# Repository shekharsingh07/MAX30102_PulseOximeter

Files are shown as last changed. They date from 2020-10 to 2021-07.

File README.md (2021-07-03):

## **Project Name:** MAX30102 Fingertip Pulse Oximeter

**Table of Contents:**
<ol>
  <li>Description</li>
  <li>License</li>
</ol>

**Description:** <br>For my undergraduate thesis, I designed a PCB for a fingertip Pulse oximeter. The pulse oximeter would use Maxim Integrated's MAX30102 biometric sensor and is created for 24hr monitoring.
<br>The project is divided into two sections:
<ol>
  <li>The embbeded software design:
    <ul>
      <li>Which is further subdivided into sections based on the components - the memory, the I/O system, and the sensor</li>
      <li>The embedded design revolves around the STM32G071RB microcontroller</li>
    </ul>
  </li>
  <li>The PCB design:
    <ul>
      <li>Which contains the necessary files to manufacture this Pulse Oximeter PCB.</li>
    </ul>
  </li>
</ol>

**License:** MIT license

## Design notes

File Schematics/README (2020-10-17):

The schematics and PCB designs have been done using KiCAD.

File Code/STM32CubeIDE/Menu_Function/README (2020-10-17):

This is the basic menu functinoality of the device. All code was done in STM32CubeIDE for a NUCLEO-G071RB. The end microcontroller that would be used is the STM32G071G8U6.

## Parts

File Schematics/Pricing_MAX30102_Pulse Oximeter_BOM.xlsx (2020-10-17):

Id | Designator | Package | Quantity | Designation | Supplier | Reference | Part No. | Total Components | Unit Price ($) | Price ($)
2 | C1,C4,C5 | C_0603_1608Metric | 3 | 4.7uF | Digi-Key | https://www.digikey.com/products/en?keywords=1276-1045-1-ND | 1276-1045-1-ND | 15 | 0.041 | 0.615
3 | C2,C3 | C_0603_1608Metric | 2 | 1uF | Digi-Key | https://www.digikey.com/products/en?keywords=1276-1945-1-ND | 1276-1945-1-ND | 10 | 0.029 | 0.29
4 | C6 | C_0603_1608Metric | 1 | 10uF | Digi-Key | https://www.digikey.com/products/en?keywords=1276-1119-1-ND | 1276-1119-1-ND | 5 | 0.11 | 0.55
5 | C7,C8 | C_0603_1608Metric | 2 | 0.1uF | Digi-Key | https://www.digikey.com/products/en?keywords=1276-1935-1-ND | 1276-1935-1-ND | 10 | 0.021 | 0.21
6 | D1 | LED_0603_1608Metric | 1 | RED | Digi-Key | https://www.digikey.com/products/en?keywords=732-4978-1-ND | 732-4978-1-ND | 5 | 0.14 | 0.7
7 | D4,D5,D6 | LED_0603_1608Metric | 3 | RED | Digi-Key | https://www.digikey.com/products/en?keywords=732-4978-1-ND | 732-4978-1-ND | 15 | 0.14 | 2.1
8 | F1 | C2Q250 | 1 | 250mA | Digi-Key | https://www.digikey.com/products/en?keywords=507-1086-1-ND | 507-1086-1-ND | 5 | 0.28 | 1.39
11 | IC1 | STM32G0_UFQFPN28_T1 | 1 | STM32G071G8U6 | Digi-Key | https://www.digikey.com/products/en?keywords=497-STM32G071G8U6-ND | 497-STM32G071G8U6-ND | 5 | 3.02 | 15.1
12 | J1 | USB_Micro-B_Molex_47346-0001 | 1 | USB_B_Micro | Digi-Key | https://www.digikey.com/products/en?keywords=609-4613-2-ND | 609-4613-2-ND | 1 | 0.2149 | 0.2149
19 | R1,R2,R4,R15,R16,R17,R18,R19,R21 | R_0603_1608Metric | 9 | 1.8K [ohm] | Digi-Key | https://www.digikey.com/products/en?keywords=RMCF0603JT1K80CT-ND | RMCF0603JT1K80CT-ND | 45 | 0.013 | 0.585
20 | R3,R5,R6 | R_0603_1608Metric | 3 | 10K [ohm] | Digi-Key | https://www.digikey.com/products/en?keywords=RMCF0603JT10K0CT-ND | RMCF0603JT10K0CT-ND | 15 | 0.013 | 0.195
21 | R7,R8,R9,R10,R11,R12,R13,R14,R23,R24,R25,R26 | R_0603_1608Metric | 12 | 0 ohm | Digi-Key | https://www.digikey.com/products/en?keywords=RMCF0603ZT0R00CT-ND | RMCF0603ZT0R00CT-ND | 60 | 0.1 | 6
22 | SW1,SW2 | SW_SPST_B3U-1000P | 2 | SW_Push | Digi-Key | https://www.digikey.com/products/en?keywords=SW1020CT-ND | SW1020CT-ND | 10 | 0.92 | 9.2
23 | U1 | MCP73811T-420I&slash_OT | 1 | MCP73811T-420I_OT | Digi-Key | https://www.digikey.com/products/en?keywords=MCP73811T-420I%2FOTCT-ND | MCP73811T-420I/OTCT-ND | 5 | 0.51 | 2.55
24 | U2 | MIC94310-GYM5-SOT-753 | 1 | MIC94310 | Digi-Key | https://www.digikey.com/products/en?keywords=576-4769-1-ND | 576-4769-1-ND | 5 | 0.23 | 1.15
25 | U3 | MAX30102EFD&plus_ | 1 | MAX30102EFD+ | Digi-Key | https://www.digikey.com/products/en?keywords=MAX30102EFD%2B-ND | MAX30102EFD+-ND | 5 | 7.74 | 38.7
26 | U4 | SON127P500X600X60-9N | 1 | AT45DB081E-MHN-Y | Digi-Key | https://www.digikey.com/products/en?keywords=1265-1110-ND | 1265-1110-ND | 5 | 1.64 | 8.2
27 | U5,U6 | MMBT3906-7-F | 2 | MMBT3906-7-F | Digi-Key | https://www.digikey.com/products/en?keywords=MMBT3906-FDICT-ND | MMBT3906-FDICT-ND | 10 | 0.12 | 1.2
 |  |  |  |  |  |  | Total | 231 | 15.2819 | 88.9499

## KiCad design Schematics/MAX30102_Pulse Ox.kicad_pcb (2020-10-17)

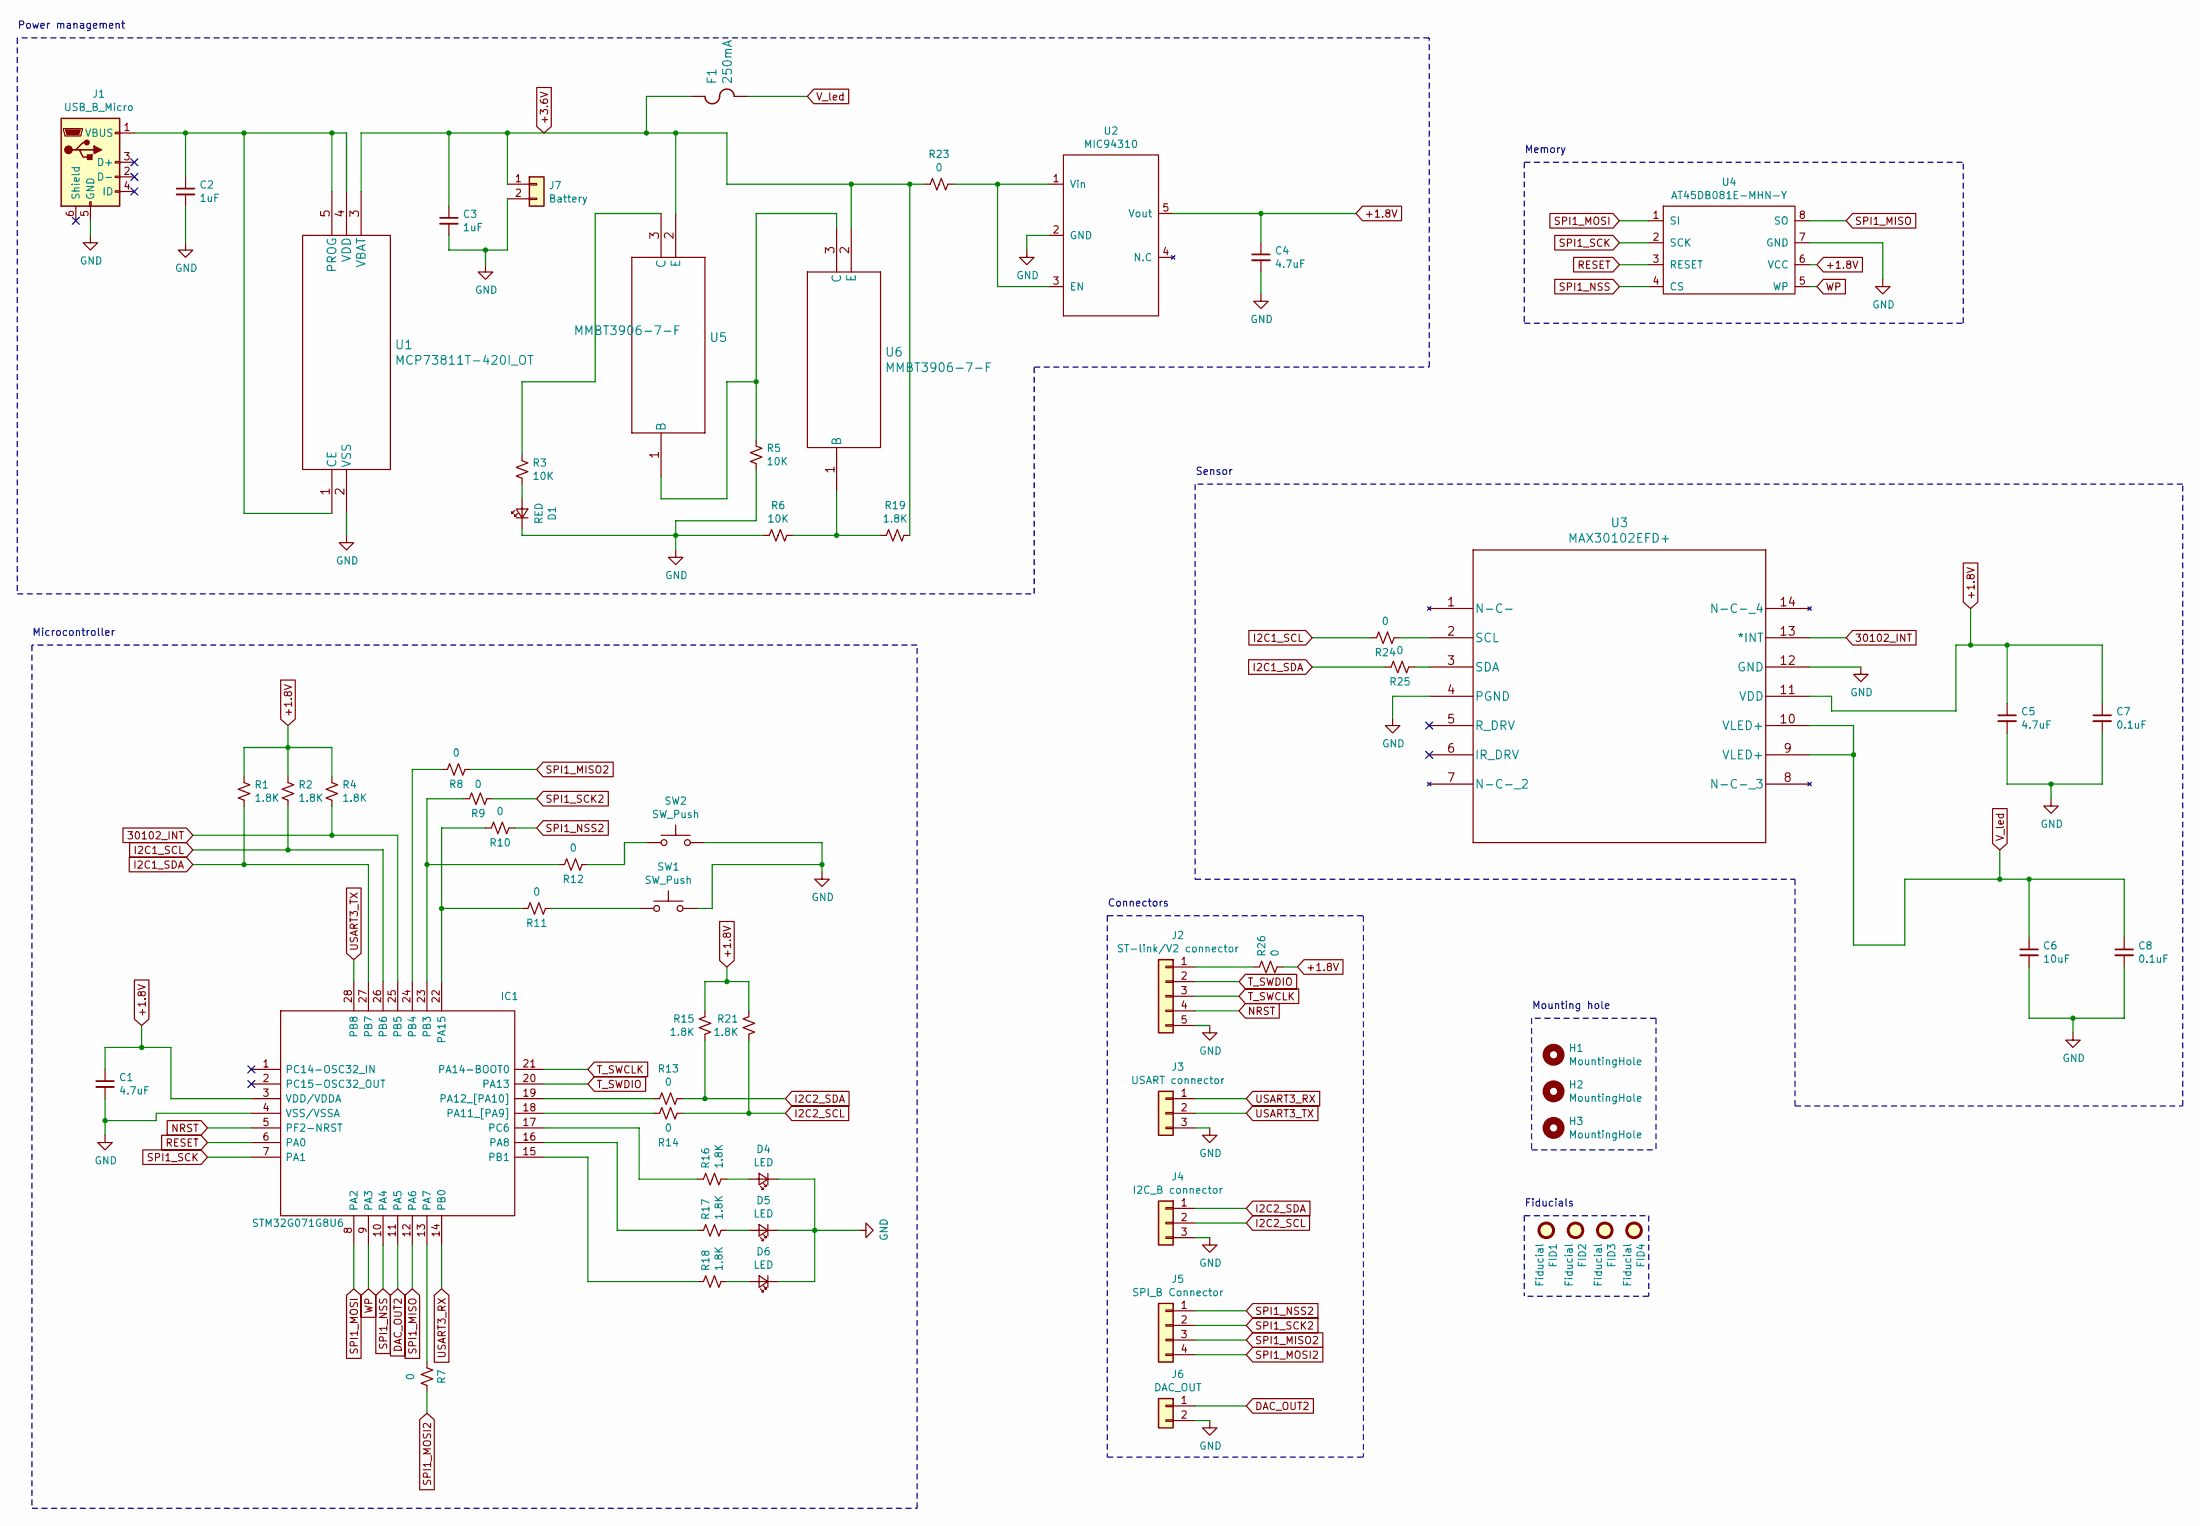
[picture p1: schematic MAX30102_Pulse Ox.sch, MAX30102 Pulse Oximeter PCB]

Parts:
C1, C4, C5: 4.7uF; C_0603_1608Metric
C2, C3: 1uF; C_0603_1608Metric
C6: 10uF; C_0603_1608Metric
C7, C8: 0.1uF; C_0603_1608Metric
D1: RED; LED_0603_1608Metric
D4, D5, D6: LED; LED_0603_1608Metric
F1: 250mA; C2Q250
FID1, FID2, FID3, FID4: Fiducial; Fiducial_1mm_Mask2mm
H1, H2, H3: MountingHole; MountingHole_2.1mm
IC1: STM32G071G8U6; STM32G0_UFQFPN28_T1; Manufacturer_Part_Number STM32G071G8U6; Mouser Part Number 511-STM32G071G8U6
J1: USB_B_Micro; USB_Micro-B_Molex_47346-0001
J2: ST-link/V2 connector; SolderWirePad_1x05_SMD
J3: USART connector; SolderWirePad_1x03_SMD
J4: I2C_B connector; SolderWirePad_1x03_SMD
J5: SPI_B Connector; SolderWirePad_1x04_SMD
J6: DAC_OUT; SolderWirePad_1x02_SMD
J7: Battery; SolderWirePad_1x02_SMD
R1, R2, R4, R15, R16, R17, R18, R19, R21: 1.8K; R_0603_1608Metric
R3, R5, R6: 10K; R_0603_1608Metric
R7, R8, R9, R10, R11, R12, R13, R14, R23, R24, R25, R26: 0; R_0603_1608Metric
SW1, SW2: SW_Push; SW_SPST_B3U-1000P
U1: MCP73811T-420I_OT; MCP73811T-420I&slash_OT
U2: MIC94310; MIC94310-GYM5-SOT-753
U3: MAX30102EFD+; MAX30102EFD&plus_
U4: AT45DB081E-MHN-Y; SON127P500X600X60-9N
U5, U6: MMBT3906-7-F

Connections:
30102_INT: IC1.25 (PB5), R4.2, U3.13 (*INT)
+1.8V: C1.1, C4.1, C5.1, C7.1, IC1.3 (VDD/VDDA), R1.1, R2.1, R4.1, R15.1, R21.1, R26.2, U2.5 (Vout), U3.11 (VDD), U4.6 (VCC)
+3.6V: C3.1, F1.2, J7.1, R19.1, R23.2, U1.3 (VBAT), U5.2 (E), U6.2 (E)
DAC_OUT2: IC1.11 (PA5), J6.1
GND: C1.2, C2.2, C3.2, C4.2, C5.2, C6.2, C7.2, C8.2, D1.1 (K), D4.1 (K), D5.1 (K), D6.1 (K), IC1.4 (VSS/VSSA), J1.5 (GND), J2.5, J3.3, J4.3, J6.2, J7.2, R5.2, R6.2, SW1.2, SW2.2, U1.2 (VSS), U2.2 (GND), U3.4 (PGND), U3.12 (GND), U4.7 (GND)
I2C1_SCL: IC1.26 (PB6), R2.2, R24.1
I2C1_SDA: IC1.27 (PB7), R1.2, R25.1
I2C2_SCL: J4.2, R14.2, R21.2
I2C2_SDA: J4.1, R13.2, R15.2
NRST: IC1.5 (PF2-NRST), J2.4
unnamed: C2.1, J1.1 (VBUS), U1.1 (CE), U1.4 (VDD), U1.5 (PROG)
unnamed: D1.2 (A), R3.2
unnamed: D4.2 (A), R16.1
unnamed: D5.2 (A), R17.1
unnamed: D6.2 (A), R18.1
unnamed: IC1.13 (PA7), R7.2
unnamed: IC1.15 (PB1), R18.2
unnamed: IC1.16 (PA8), R17.2
unnamed: IC1.17 (PC6), R16.2
unnamed: IC1.18 (PA11_[PA9]), R14.1
unnamed: IC1.19 (PA12_[PA10]), R13.1
unnamed: IC1.22 (PA15), R10.1, R11.1
unnamed: IC1.23 (PB3), R9.1, R12.1
unnamed: IC1.24 (PB4), R8.1
unnamed: J2.1, R26.1
unnamed: R3.1, U5.3 (C)
unnamed: R5.1, U5.1 (B), U6.3 (C)
unnamed: R11.2, SW1.1
unnamed: R12.2, SW2.1
unnamed: R6.1, R19.2, U6.1 (B)
unnamed: R23.1, U2.1 (Vin), U2.3 (EN)
unnamed: R24.2, U3.2 (SCL)
unnamed: R25.2, U3.3 (SDA)
RESET: IC1.6 (PA0), U4.3 (RESET)
SPI1_MISO: IC1.12 (PA6), U4.8 (SO)
SPI1_MISO2: J5.3, R8.2
SPI1_MOSI: IC1.8 (PA2), U4.1 (SI)
SPI1_MOSI2: J5.4, R7.1
SPI1_NSS: IC1.10 (PA4), U4.4 (CS)
SPI1_NSS2: J5.1, R10.2
SPI1_SCK: IC1.7 (PA1), U4.2 (SCK)
SPI1_SCK2: J5.2, R9.2
T_SWCLK: IC1.21 (PA14-BOOT0), J2.3
T_SWDIO: IC1.20 (PA13), J2.2
USART3_RX: IC1.14 (PB0), J3.1
USART3_TX: IC1.28 (PB8), J3.2
V_led: C6.1, C8.1, F1.1, U3.9 (VLED+), U3.10 (VLED+)
WP: IC1.9 (PA3), U4.5 (WP)

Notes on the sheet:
Microcontroller
Power management
Connectors
Sensor
Memory
Mounting hole
Fiducials

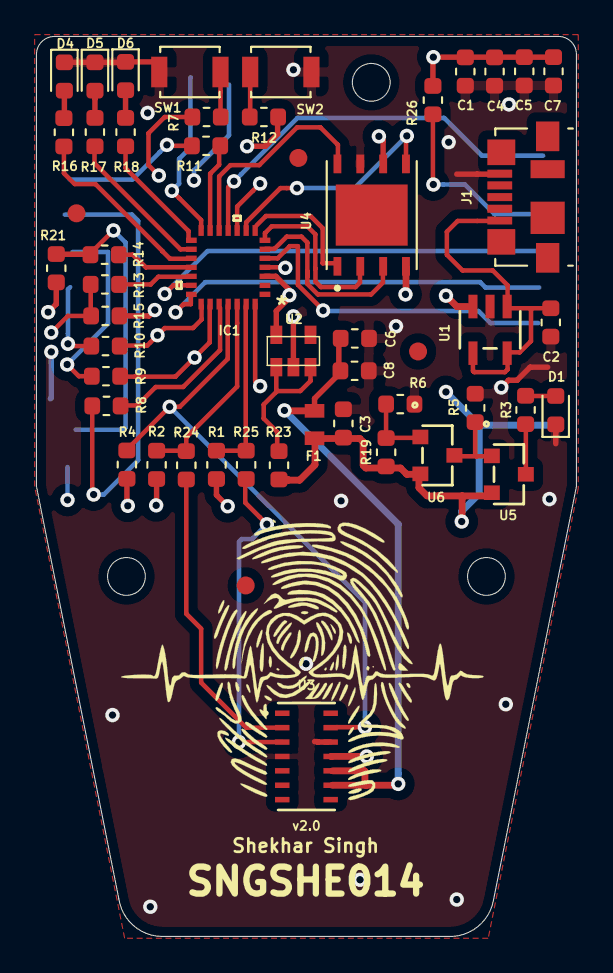
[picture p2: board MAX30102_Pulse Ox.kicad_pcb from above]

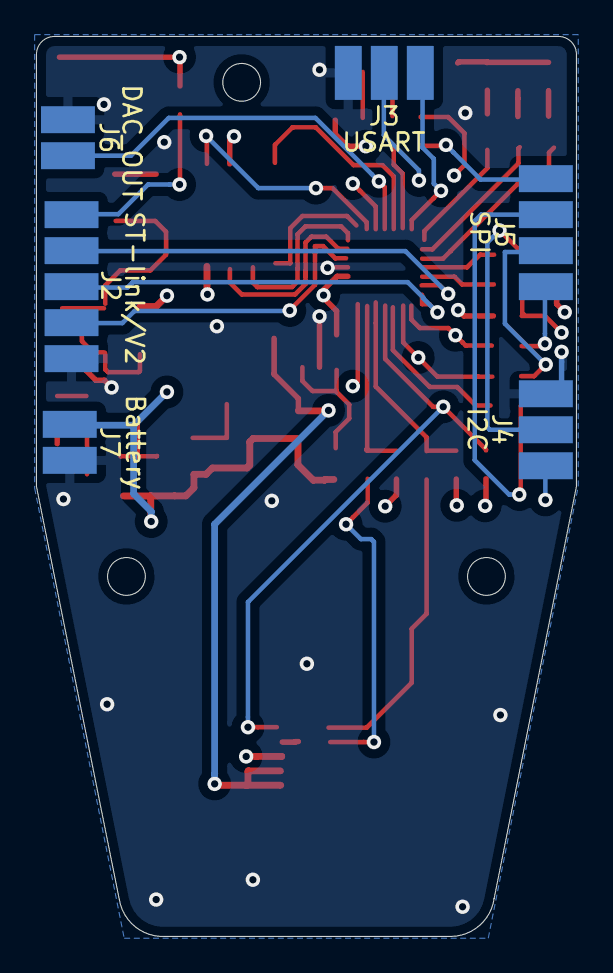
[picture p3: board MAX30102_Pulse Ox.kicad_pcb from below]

Board: 4 copper layers, 30.0 x 50.0 mm, 60 parts (6 on the bottom side), 48 nets.

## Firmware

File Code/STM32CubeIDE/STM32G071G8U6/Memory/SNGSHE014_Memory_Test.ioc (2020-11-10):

#MicroXplorer Configuration settings - do not modify
File.Version=6
GPIO.groupedBy=Group By Peripherals
KeepUserPlacement=false
Mcu.Family=STM32G0
Mcu.IP0=NVIC
Mcu.IP1=RCC
Mcu.IP2=SPI1
Mcu.IP3=SYS
Mcu.IP4=USART3
Mcu.IPNb=5
Mcu.Name=STM32G071G(6-8-B)Ux
Mcu.Package=UFQFPN28
Mcu.Pin0=PA0
Mcu.Pin1=PA1
Mcu.Pin2=PA2
Mcu.Pin3=PA3
Mcu.Pin4=PA4
Mcu.Pin5=PA6
Mcu.Pin6=PB0
Mcu.Pin7=PB8
Mcu.Pin8=VP_SYS_VS_Systick
Mcu.Pin9=VP_SYS_VS_DBSignals
Mcu.PinsNb=10
Mcu.ThirdPartyNb=0
Mcu.UserConstants=
Mcu.UserName=STM32G071G8Ux
MxCube.Version=6.0.1
MxDb.Version=DB.6.0.0
NVIC.ForceEnableDMAVector=true
NVIC.HardFault_IRQn=true\:0\:0\:false\:false\:true\:false\:false
NVIC.NonMaskableInt_IRQn=true\:0\:0\:false\:false\:true\:false\:false
NVIC.PendSV_IRQn=true\:0\:0\:false\:false\:true\:false\:false
NVIC.SPI1_IRQn=true\:0\:0\:false\:false\:true\:true\:true
NVIC.SVC_IRQn=true\:0\:0\:false\:false\:true\:false\:false
NVIC.SysTick_IRQn=true\:0\:0\:false\:false\:true\:false\:true
NVIC.USART3_4_LPUART1_IRQn=true\:0\:0\:false\:false\:true\:true\:true
PA0.GPIOParameters=GPIO_Label
PA0.GPIO_Label=RESET
PA0.Locked=true
PA0.Signal=GPIO_Output
PA1.Mode=Full_Duplex_Master
PA1.Signal=SPI1_SCK
PA2.Mode=Full_Duplex_Master
PA2.Signal=SPI1_MOSI
PA3.GPIOParameters=GPIO_Label
PA3.GPIO_Label=WP
PA3.Locked=true
PA3.Signal=GPIO_Output
PA4.Mode=NSS_Signal_Hard_Output
PA4.Signal=SPI1_NSS
PA6.Mode=Full_Duplex_Master
PA6.Signal=SPI1_MISO
PB0.Mode=Asynchronous
PB0.Signal=USART3_RX
PB8.Locked=true
PB8.Mode=Asynchronous
PB8.Signal=USART3_TX
PinOutPanel.RotationAngle=0
ProjectManager.AskForMigrate=true
ProjectManager.BackupPrevious=false
ProjectManager.CompilerOptimize=6
ProjectManager.ComputerToolchain=false
ProjectManager.CoupleFile=false
ProjectManager.CustomerFirmwarePackage=
ProjectManager.DefaultFWLocation=true
ProjectManager.DeletePrevious=true
ProjectManager.DeviceId=STM32G071G8Ux
ProjectManager.FirmwarePackage=STM32Cube FW_G0 V1.3.0
ProjectManager.FreePins=false
ProjectManager.HalAssertFull=false
ProjectManager.HeapSize=0x200
ProjectManager.KeepUserCode=true
ProjectManager.LastFirmware=true
ProjectManager.LibraryCopy=1
ProjectManager.MainLocation=Core/Src
ProjectManager.NoMain=false
ProjectManager.PreviousToolchain=STM32CubeIDE
ProjectManager.ProjectBuild=false
ProjectManager.ProjectFileName=SNGSHE014_Memory_Test.ioc
ProjectManager.ProjectName=SNGSHE014_Memory_Test
ProjectManager.RegisterCallBack=
ProjectManager.StackSize=0x400
ProjectManager.TargetToolchain=STM32CubeIDE
ProjectManager.ToolChainLocation=
ProjectManager.UnderRoot=true
ProjectManager.functionlistsort=1-MX_GPIO_Init-GPIO-false-HAL-true,2-SystemClock_Config-RCC-false-HAL-false,3-MX_SPI1_Init-SPI1-false-HAL-true,4-MX_USART3_UART_Init-USART3-false-HAL-true
RCC.AHBFreq_Value=16000000
RCC.APBFreq_Value=16000000
RCC.APBTimFreq_Value=16000000
RCC.CECFreq_Value=32786.88524590164
RCC.CortexFreq_Value=16000000
RCC.EXTERNAL_CLOCK_VALUE=48000
RCC.FCLKCortexFreq_Value=16000000
RCC.FamilyName=M
RCC.HCLKFreq_Value=16000000
RCC.HSE_VALUE=8000000
RCC.HSI_VALUE=16000000
RCC.I2C1Freq_Value=16000000
RCC.I2S1Freq_Value=16000000
RCC.IPParameters=AHBFreq_Value,APBFreq_Value,APBTimFreq_Value,CECFreq_Value,CortexFreq_Value,EXTERNAL_CLOCK_VALUE,FCLKCortexFreq_Value,FamilyName,HCLKFreq_Value,HSE_VALUE,HSI_VALUE,I2C1Freq_Value,I2S1Freq_Value,LPTIM1Freq_Value,LPTIM2Freq_Value,LPUART1Freq_Value,LSCOPinFreq_Value,LSE_VALUE,LSI_VALUE,MCO1PinFreq_Value,PLLPoutputFreq_Value,PLLQoutputFreq_Value,PLLRCLKFreq_Value,PWRFreq_Value,SYSCLKFreq_VALUE,TIM15Freq_Value,TIM1Freq_Value,USART1Freq_Value,USART2Freq_Value,VCOInputFreq_Value,VCOOutputFreq_Value
RCC.LPTIM1Freq_Value=16000000
RCC.LPTIM2Freq_Value=16000000
RCC.LPUART1Freq_Value=16000000
RCC.LSCOPinFreq_Value=32000
RCC.LSE_VALUE=32768
RCC.LSI_VALUE=32000
RCC.MCO1PinFreq_Value=16000000
RCC.PLLPoutputFreq_Value=64000000
RCC.PLLQoutputFreq_Value=64000000
RCC.PLLRCLKFreq_Value=64000000
RCC.PWRFreq_Value=16000000
RCC.SYSCLKFreq_VALUE=16000000
RCC.TIM15Freq_Value=16000000
RCC.TIM1Freq_Value=16000000
RCC.USART1Freq_Value=16000000
RCC.USART2Freq_Value=16000000
RCC.VCOInputFreq_Value=16000000
RCC.VCOOutputFreq_Value=128000000
SPI1.CalculateBaudRate=8.0 MBits/s
SPI1.Direction=SPI_DIRECTION_2LINES
SPI1.IPParameters=VirtualType,Mode,Direction,CalculateBaudRate,VirtualNSS
SPI1.Mode=SPI_MODE_MASTER
SPI1.VirtualNSS=VM_NSSHARD
SPI1.VirtualType=VM_MASTER
USART3.IPParameters=VirtualMode-Asynchronous
USART3.VirtualMode-Asynchronous=VM_ASYNC
VP_SYS_VS_DBSignals.Mode=DisableDeadBatterySignals
VP_SYS_VS_DBSignals.Signal=SYS_VS_DBSignals
VP_SYS_VS_Systick.Mode=SysTick
VP_SYS_VS_Systick.Signal=SYS_VS_Systick
board=custom
isbadioc=false

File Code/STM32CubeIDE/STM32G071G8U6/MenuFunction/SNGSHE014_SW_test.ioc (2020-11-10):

#MicroXplorer Configuration settings - do not modify
File.Version=6
GPIO.groupedBy=Group By Peripherals
KeepUserPlacement=false
Mcu.Family=STM32G0
Mcu.IP0=NVIC
Mcu.IP1=RCC
Mcu.IP2=SYS
Mcu.IP3=TIM14
Mcu.IP4=USART3
Mcu.IPNb=5
Mcu.Name=STM32G071G(6-8-B)Ux
Mcu.Package=UFQFPN28
Mcu.Pin0=PC14-OSC32_IN (PC14)
Mcu.Pin1=PC15-OSC32_OUT (PC15)
Mcu.Pin10=PB8
Mcu.Pin11=VP_SYS_VS_Systick
Mcu.Pin12=VP_SYS_VS_DBSignals
Mcu.Pin13=VP_TIM14_VS_ClockSourceINT
Mcu.Pin2=PA4
Mcu.Pin3=PB0
Mcu.Pin4=PB1
Mcu.Pin5=PA8
Mcu.Pin6=PA13
Mcu.Pin7=PA14-BOOT0
Mcu.Pin8=PA15
Mcu.Pin9=PB3
Mcu.PinsNb=14
Mcu.ThirdPartyNb=0
Mcu.UserConstants=
Mcu.UserName=STM32G071G8Ux
MxCube.Version=6.0.1
MxDb.Version=DB.6.0.0
NVIC.EXTI2_3_IRQn=true\:1\:0\:true\:false\:true\:true\:true
NVIC.EXTI4_15_IRQn=true\:1\:0\:true\:false\:true\:true\:true
NVIC.ForceEnableDMAVector=true
NVIC.HardFault_IRQn=true\:0\:0\:false\:false\:true\:false\:false
NVIC.NonMaskableInt_IRQn=true\:0\:0\:false\:false\:true\:false\:false
NVIC.PendSV_IRQn=true\:0\:0\:false\:false\:true\:false\:false
NVIC.SVC_IRQn=true\:0\:0\:false\:false\:true\:false\:false
NVIC.SysTick_IRQn=true\:0\:0\:false\:false\:true\:false\:true
NVIC.TIM14_IRQn=true\:0\:0\:false\:false\:true\:true\:true
PA13.Locked=true
PA13.Mode=Serial_Wire
PA13.Signal=SYS_SWDIO
PA14-BOOT0.Mode=Serial_Wire
PA14-BOOT0.Signal=SYS_SWCLK
PA15.GPIOParameters=GPIO_PuPd,GPIO_Label,GPIO_ModeDefaultEXTI
PA15.GPIO_Label=SW1
PA15.GPIO_ModeDefaultEXTI=GPIO_MODE_IT_RISING_FALLING
PA15.GPIO_PuPd=GPIO_PULLUP
PA15.Locked=true
PA15.Signal=GPXTI15
PA4.Mode=SYS_WakeUp1
PA4.Signal=SYS_WKUP2
PA8.GPIOParameters=PinState,GPIO_PuPd,GPIO_Label
PA8.GPIO_Label=LED1
PA8.GPIO_PuPd=GPIO_PULLUP
PA8.Locked=true
PA8.PinState=GPIO_PIN_RESET
PA8.Signal=GPIO_Output
PB0.Locked=true
PB0.Mode=Asynchronous
PB0.Signal=USART3_RX
PB1.GPIOParameters=GPIO_PuPd,GPIO_Label
PB1.GPIO_Label=LED2
PB1.GPIO_PuPd=GPIO_PULLUP
PB1.Locked=true
PB1.Signal=GPIO_Output
PB3.GPIOParameters=GPIO_PuPd,GPIO_Label,GPIO_ModeDefaultEXTI
PB3.GPIO_Label=SW2
PB3.GPIO_ModeDefaultEXTI=GPIO_MODE_IT_RISING_FALLING
PB3.GPIO_PuPd=GPIO_PULLUP
PB3.Locked=true
PB3.Signal=GPXTI3
PB8.Locked=true
PB8.Mode=Asynchronous
PB8.Signal=USART3_TX
PC14-OSC32_IN\ (PC14).Mode=LSE-External-Oscillator
PC14-OSC32_IN\ (PC14).Signal=RCC_OSC32_IN
PC15-OSC32_OUT\ (PC15).Mode=LSE-External-Oscillator
PC15-OSC32_OUT\ (PC15).Signal=RCC_OSC32_OUT
PinOutPanel.RotationAngle=0
ProjectManager.AskForMigrate=true
ProjectManager.BackupPrevious=false
ProjectManager.CompilerOptimize=6
ProjectManager.ComputerToolchain=false
ProjectManager.CoupleFile=false
ProjectManager.CustomerFirmwarePackage=
ProjectManager.DefaultFWLocation=true
ProjectManager.DeletePrevious=true
ProjectManager.DeviceId=STM32G071G8Ux
ProjectManager.FirmwarePackage=STM32Cube FW_G0 V1.3.0
ProjectManager.FreePins=false
ProjectManager.HalAssertFull=false
ProjectManager.HeapSize=0x200
ProjectManager.KeepUserCode=true
ProjectManager.LastFirmware=true
ProjectManager.LibraryCopy=1
ProjectManager.MainLocation=Core/Src
ProjectManager.NoMain=false
ProjectManager.PreviousToolchain=
ProjectManager.ProjectBuild=false
ProjectManager.ProjectFileName=SNGSHE014_SW_test.ioc
ProjectManager.ProjectName=SNGSHE014_SW_test
ProjectManager.RegisterCallBack=
ProjectManager.StackSize=0x400
ProjectManager.TargetToolchain=STM32CubeIDE
ProjectManager.ToolChainLocation=
ProjectManager.UnderRoot=true
ProjectManager.functionlistsort=1-MX_GPIO_Init-GPIO-false-HAL-true,2-SystemClock_Config-RCC-false-HAL-false,3-MX_TIM14_Init-TIM14-false-HAL-true,4-MX_USART1_Init-USART1-false-HAL-true,5-MX_USART3_UART_Init-USART3-false-HAL-true
RCC.AHBFreq_Value=16000000
RCC.APBFreq_Value=16000000
RCC.APBTimFreq_Value=16000000
RCC.CECFreq_Value=32786.88524590164
RCC.CortexFreq_Value=16000000
RCC.EXTERNAL_CLOCK_VALUE=48000
RCC.FCLKCortexFreq_Value=16000000
RCC.FamilyName=M
RCC.HCLKFreq_Value=16000000
RCC.HSE_VALUE=8000000
RCC.HSI_VALUE=16000000
RCC.I2C1Freq_Value=16000000
RCC.I2S1Freq_Value=16000000
RCC.IPParameters=AHBFreq_Value,APBFreq_Value,APBTimFreq_Value,CECFreq_Value,CortexFreq_Value,EXTERNAL_CLOCK_VALUE,FCLKCortexFreq_Value,FamilyName,HCLKFreq_Value,HSE_VALUE,HSI_VALUE,I2C1Freq_Value,I2S1Freq_Value,LPTIM1Freq_Value,LPTIM2Freq_Value,LPUART1Freq_Value,LSCOPinFreq_Value,LSI_VALUE,MCO1PinFreq_Value,PLLPoutputFreq_Value,PLLQoutputFreq_Value,PLLRCLKFreq_Value,PWRFreq_Value,SYSCLKFreq_VALUE,TIM15Freq_Value,TIM1Freq_Value,USART1Freq_Value,USART2Freq_Value,VCOInputFreq_Value,VCOOutputFreq_Value
RCC.LPTIM1Freq_Value=16000000
RCC.LPTIM2Freq_Value=16000000
RCC.LPUART1Freq_Value=16000000
RCC.LSCOPinFreq_Value=32000
RCC.LSI_VALUE=32000
RCC.MCO1PinFreq_Value=16000000
RCC.PLLPoutputFreq_Value=64000000
RCC.PLLQoutputFreq_Value=64000000
RCC.PLLRCLKFreq_Value=64000000
RCC.PWRFreq_Value=16000000
RCC.SYSCLKFreq_VALUE=16000000
RCC.TIM15Freq_Value=16000000
RCC.TIM1Freq_Value=16000000
RCC.USART1Freq_Value=16000000
RCC.USART2Freq_Value=16000000
RCC.VCOInputFreq_Value=16000000
RCC.VCOOutputFreq_Value=128000000
SH.GPXTI15.0=GPIO_EXTI15
SH.GPXTI15.ConfNb=1
SH.GPXTI3.0=GPIO_EXTI3
SH.GPXTI3.ConfNb=1
TIM14.IPParameters=Prescaler,Period
TIM14.Period=65535-1
TIM14.Prescaler=16000-1
USART3.IPParameters=VirtualMode-Asynchronous
USART3.VirtualMode-Asynchronous=VM_ASYNC
VP_SYS_VS_DBSignals.Mode=DisableDeadBatterySignals
VP_SYS_VS_DBSignals.Signal=SYS_VS_DBSignals
VP_SYS_VS_Systick.Mode=SysTick
VP_SYS_VS_Systick.Signal=SYS_VS_Systick
VP_TIM14_VS_ClockSourceINT.Mode=Enable_Timer
VP_TIM14_VS_ClockSourceINT.Signal=TIM14_VS_ClockSourceINT
board=custom
isbadioc=false

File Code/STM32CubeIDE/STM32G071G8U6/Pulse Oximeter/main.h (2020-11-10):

/* USER CODE BEGIN Header */
/**
  ******************************************************************************
  * @file           : main.h
  * @brief          : Header for main.c file.
  *                   This file contains the common defines of the application.
  ******************************************************************************
  * @attention
  *
  * <h2><center>&copy; Copyright (c) 2020 STMicroelectronics.
  * All rights reserved.</center></h2>
  *
  * This software component is licensed by ST under BSD 3-Clause license,
  * the "License"; You may not use this file except in compliance with the
  * License. You may obtain a copy of the License at:
  *                        opensource.org/licenses/BSD-3-Clause
  *
  ******************************************************************************
  */
/* USER CODE END Header */

/* Define to prevent recursive inclusion -------------------------------------*/
#ifndef __MAIN_H
#define __MAIN_H

#ifdef __cplusplus
extern "C" {
#endif

/* Includes ------------------------------------------------------------------*/
#include "stm32g0xx_hal.h"

/* Private includes ----------------------------------------------------------*/
/* USER CODE BEGIN Includes */

/* USER CODE END Includes */

/* Exported types ------------------------------------------------------------*/
/* USER CODE BEGIN ET */

/* USER CODE END ET */

/* Exported constants --------------------------------------------------------*/
/* USER CODE BEGIN EC */

/* USER CODE END EC */

/* Exported macro ------------------------------------------------------------*/
/* USER CODE BEGIN EM */

/* USER CODE END EM */

/* Exported functions prototypes ---------------------------------------------*/
void Error_Handler(void);

/* USER CODE BEGIN EFP */

/* USER CODE END EFP */

/* Private defines -----------------------------------------------------------*/
#define LED3_Pin GPIO_PIN_1
#define LED3_GPIO_Port GPIOB
#define LED2_Pin GPIO_PIN_8
#define LED2_GPIO_Port GPIOA
#define LED1_Pin GPIO_PIN_6
#define LED1_GPIO_Port GPIOC
#define SW1_Pin GPIO_PIN_15
#define SW1_GPIO_Port GPIOA
#define SW2_Pin GPIO_PIN_3
#define SW2_GPIO_Port GPIOB
#define INT_Pin GPIO_PIN_5
#define INT_GPIO_Port GPIOB
#define SCL_Pin GPIO_PIN_6
#define SCL_GPIO_Port GPIOB
#define SDA_Pin GPIO_PIN_7
#define SDA_GPIO_Port GPIOB
/* USER CODE BEGIN Private defines */

/* USER CODE END Private defines */

#ifdef __cplusplus
}
#endif

#endif /* __MAIN_H */

/************************ (C) COPYRIGHT STMicroelectronics *****END OF FILE****/

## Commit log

2020-10-17 Add files via upload
    KiCAD project files
    [BOM_MAX30102_Pulse Ox.csv, MAX30102_Pulse Ox-B_Cu.gbr, MAX30102_Pulse Ox-B_Mask.gbr, MAX30102_Pulse Ox-B_SilkS.gbr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]
2020-11-10 Create STM32G071x_MAX30102 sensor
2020-11-10 Add files via upload
    The project folders for the MAX30102 sensor

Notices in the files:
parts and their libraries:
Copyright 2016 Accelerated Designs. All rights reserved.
